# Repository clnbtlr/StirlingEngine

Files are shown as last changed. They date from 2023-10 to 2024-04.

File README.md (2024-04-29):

# StirlingEngine

Repository for the thermodynamic analysis of desktop Stirling engine. An Arduino micro is used to measure the engines internal pressure and flywheel angle. This data is then imported into matlab to determine the heat, work and thermal efficiency. This project is intended as a low-cost demonstration of the different thermodynamic processes in an actual heat engine for physics or engineering students.

Front view:


 
Top view:



## Bill of Materials

| Part                                            | Supplier     | Cost, each (€)|
| ----------------------------------------------- | ------------ |---------------|
| Stirling Engine                                 | Amazon       | 40            |
| Arduino micro                                   | RS           | 26            |
| Mikro-2755 Angle 3 Breakout board               | RS           | 14            |
| MPXV7002DPT1 Pressure Sensor                    | Farnell      | 18            |
| Perma-Proto small mint tin size breadboard      | Adafruit     | 8             |
| Pnuematic tube adapter M5 Male to Push In 4 mm  | RS           | 3             |
| Diametrically magnetised ring magnet Ø 10/5 mm  | supermagnete | 1             |

An Arduino micro was used as it operates at 5V which is the voltage required for the pressure and angle sensors but this could also be substituted for an Arduino Uno.

As well as the above, jumper wires of various lengths, male hearder pins, 4 x M3 screws, and a small length (~ 7 cm) of Ø 4 mm pneumatic tubing are also required.

In addition, some small 3d-printed PLA parts were used. The .stl files are included in the .\stlFiles directory.

| 3d-printed part name     | Qty required |
| ------------------------ | ------------ |
| MagnetHolder.stl         | 1            |
| PermaProtoSmallClip.stl  | 2            |

## Assembly

The pressure sensor was soldered to the perma-proto board such that pin 2 (Vs) and pin 3 (GND) are along the positive and negative power rails. 7 male header pins were soldered in row 3, columns 0-6. Jumper wires were then soldered in place to connect the pressure sensor pins and angle 3 breakout board to the header pins, as shown in the front view photo.

The pinout for the connections is as follows: 

| Arduino micro            | Angle 3 click/AK7451 | MPXV7002DPT1 | Perma-Proto pin |
| ------------------------ | -------------------- | ------------ | --------------- |
| 5V   | 5V  | Vs   | 2 |
| GND  | GND | GND  | 1 |
| SCK  | SCK | -    | 5 |
| MI   | SDO | -    | 4 |
| MO   | SDI | -    | 3 |
| SS   | CS  | -    | 6 |
| A5   | -   | Vout | 0 |

A M5 hole was drilled and taped into the top plate of the engine and the pneumatic adapter with gasket was screwed in place.

The MagnetHolder 3d-printed part acts as a bushing between the ring magnet and the shaft of the flywheel. The magnet was glued onto the 3d-printed part before being pushed onto the shaft up to the cam. See top view photo. No glue was used as the PLA part is intended to be a tight fit.

The 2 x PermaProtoSmallClip 3d-printed parts are used with the 4 x M3 screws to secure the soldered breadboard to the metal vertical bracket. The PLA parts are designed to be self-taped by the M3 screws. Ensure that the AK7451 chip on the Angle 3 click board is lined up with the flywheel axis of rotation, and then tighten the M3 screws sufficiently so everything doesn't move.

Connect the Ø 4 mm pneumatic tubing to the MPXV7002DPT1 pressure sensor port closest to its top surface (port P1 in its datasheet) and the pneumatic adapter in the top plate.

## Arduino Code

The zero position of the angle sensor needs to be set correctly so that during operation, the measured angle increases. The zero position is the angle reading corresponding to the highest point of piston in degrees. It will vary based on how the magnet was assembled to the flywheel shaft. Using the Arduino IDE, uncomment the Serial.print(angle) line in the stirlingEngine.ino sketch and upload it to the Arduino micro.

Slowly rotate the flywheel by hand until the piston is at its maximum height, read the angle value in the Serial monitor and then update the zeroPos variable in the sketch. The Serial.print(angle) line can be commented out now again. Update the geometric variables in the script if necessary for a different model of Stirling engine. Upload the updated sketch to the Arduino micro again.

The real-time values for the pressure and volume can now be monitored in the Serial Plotter window.

## Running a test

Fill a mug with hot water from a kettle. Measure its temperature (i.e. the hot reservoir temperature) using a thermometer/thermistor/thermocouple. Measure ambient temperature (i.e. the cold reservoir temperature). Place the Stirling engine on top of the mug and wait a few minutes for the hot plate to heat up. Then by hand, spin the flywheel and it should start running freely. Direction of rotation is clockwise in the photos above.

The almost sinusodial change in pressure and volume over time should be observed in the Ardunio IDE serial plotter window. The pressure signal leads the volume signal.

## Data analysis with Matlab

In the Matlab script readStirlingData.m (tested on r2019b and r2023a), the measurements from the Arduino can be streamed using serial port communication using the Instrument Control Toolbox (in the absence of this toolbox, the data from the Arduino serial port could also be recorded to a .txt file using PuTTY and then imported into Matlab). The gauge pressure and volume change data for ~12 seconds or ~30 cycles are saved in a .mat file for loading. Two .mat files of data from the Arduino are provided in this repository:

| .mat file name           | Description                               |
| ------------------------ | ----------------------------------------- |
| arduinoData.mat          | P and V data from MPXV7002 sensor         |
| arduinoData1.mat         | P and V data from PSE533 sensor           |

The PSE533 pressure sensor was used to compare/check the values from the MPXV7002 sensor. The values of pressure were sligtly different between the two sensors, most likely as a result of sensor accuracy and precision. Either set of data can be used in the analysis.

The matlab script first plots the time series data from the arduino similar to the Arduino IDE serial plotter, as shown below.

arduinoTimeSeries

It then presents this data as a P-V diagram, with the values for pressure converted from gauge to absolute pressure, and the volume converted from dV to specific volume.

arduinoPV

The ideal Stirling cycle P-V diagram is calculated using the different thermodynamic process relationships and from the measured hot and cold reservoir temperatures and the min. and max. specific volumes. Both the ideal and measured P-v data is plotted and the results show that the actual engine is doing much less net work than the actual cycle due to inefficiencies/irreversibilities.

idealPV

The ideal Stirling cycle T-s diagram is calculated, again using the different thermodynamic process relationships, and the measured P-V data is recalculated into T and s. The values for heat, work and thermal efficiencies are calculated and output to the console. The ideal Carnot efficiency was found to be ~19% while the actual efficiency was ~0.4%.

## Data analysis with Python
The python script readStirlingData.py works in the same fashion as the matlab script. The pressure and volume data from the Arduino is imported from the data.csv file included in the directory. The P-V and T-s values are calculated and followed by plotting of the diagrams. Efficiency results are identical to the matlab results.

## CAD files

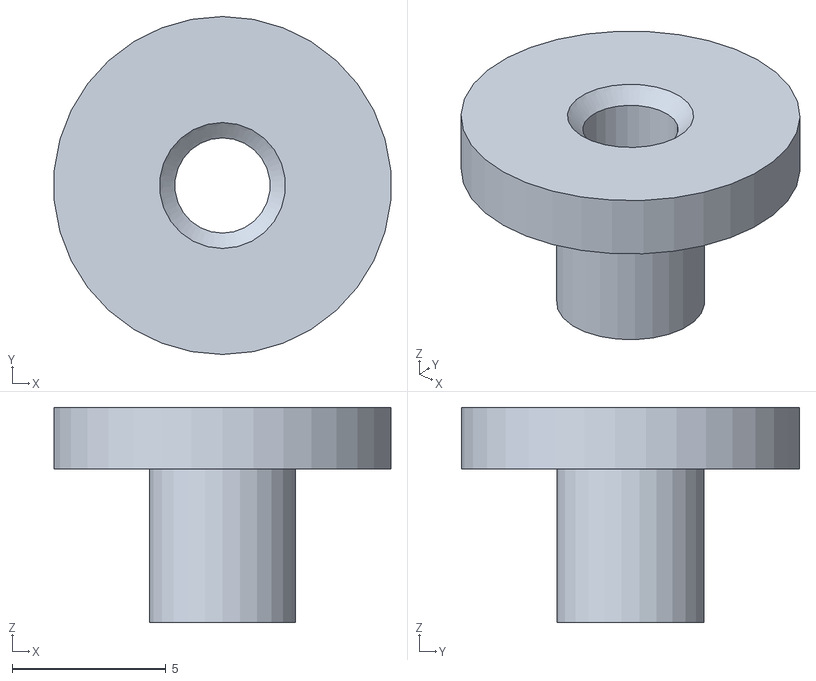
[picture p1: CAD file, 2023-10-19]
stlFiles/MagnetHolder.stl
11.0 x 11.0 x 7.00

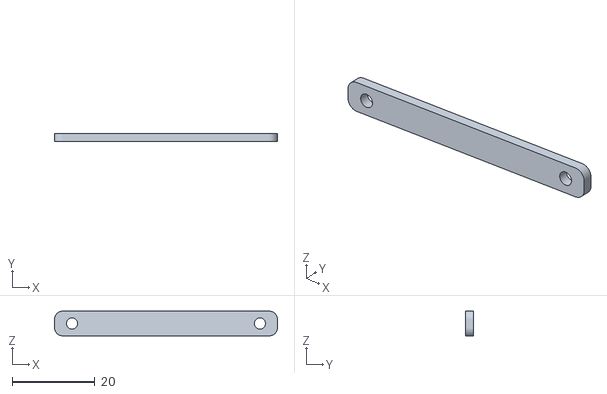
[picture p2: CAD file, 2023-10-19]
stlFiles/PermaProtoSmallClip.STL
54.0 x 2.00 x 6.00

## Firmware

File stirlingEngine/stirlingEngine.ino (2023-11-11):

/* Stirling Engine Pressure and Volume measurement. 
clnbtlr
Oct 2023

Using Arduino Micro as MCB as sensors require 5V.
Pinout:
  AK7451:
  5V <-> 5V
  GND <-> GND
  SCK <-> SCK
  MI <-> SDO
  MO <-> SDI
  SS <-> CS

  MPXV7002DPT1:
  5V <-> VS
  GND <-> GND
  A5 <-> VOUT
*/

#include <SPI.h>
#include "ak7451.h"
AK7451  ak7451;

int r = 4; // offset distance between axis and crank [mm]
int L = 40; // crank arm length [mm]
float A = PI/4.0*sq(16.0); // piston cross sectional area [mm2]
float zeroPos = 123.0; // angle reading corresponding to highest point of piston [deg]
int pressurePin = A5; // analog input pin for pressure sensor

void setup() {
  Serial.begin(19200);
  while(!Serial){ // wait for serial port
    delay(1);
  }
  Serial.println("***Reset***");
  ak7451.begin(SS); // SS pin on Arduino Micro but can be any other Digital I/O Pin
}

void loop() {
  float supply = readVcc()/1000.0; // read Vcc supply
  float angle = ak7451.readAngle(); // read angle from AK7451 sensor
  angle = fmodf(angle+zeroPos,360.0); // removes zeroPos from measured angle and wraps to 360 deg using modulo function
  float pressure = analogRead(pressurePin)*supply/1024.0; // read bits from pressure sensor and convert to voltage
  pressure = (pressure/supply-0.5)/0.2; // convert V to kPa (see MPXV7002 datasheet p.6 for transfer function)
  //pressure = ((pressure)*50.5)-151.5; // convert V to kPa (see PSE533 datasheet 3 for transfer function)
  float h = r*(cos(deg2rad(angle))-L/r*(sqrt(1-(r/L*sq(sin(deg2rad(angle)))))-1)); // change in piston height (see Lu paper, eq.2)
  float volume = A*h/1000.0; // volume change [cm3]
  //Serial.print("angle:"); Serial.print(angle); Serial.print(",");// print angle to Serial Monitor
  //Serial.print("height:");Serial.print(h,3); Serial.print(",");// print height to Serial Monitor
  Serial.print(pressure,3); Serial.print(",");
  Serial.println(volume,3); // print volume to Serial Monitor
  delay(10); // delay between measurements (Lu paper used 200 samples/sec)
}

long readVcc() { // Read supply voltage to improve ADC precision from https://github.com/SensorsIot/ADC_Test.git
  long result;
  // Read 1.1V reference against AVcc
  #if defined(__AVR_ATmega32U4__) || defined(__AVR_ATmega1280__) || defined(__AVR_ATmega2560__)
  ADMUX = _BV(REFS0) | _BV(MUX4) | _BV(MUX3) | _BV(MUX2) | _BV(MUX1);
  #elif defined (__AVR_ATtiny24__) || defined(__AVR_ATtiny44__) || defined(__AVR_ATtiny84__)
  ADMUX = _BV(MUX5) | _BV(MUX0);
  #elif defined (__AVR_ATtiny25__) || defined(__AVR_ATtiny45__) || defined(__AVR_ATtiny85__)
  ADMUX = _BV(MUX3) | _BV(MUX2);
  #else
  ADMUX = _BV(REFS0) | _BV(MUX3) | _BV(MUX2) | _BV(MUX1);
  #endif
  delay(2); // Wait for Vref to settle
  ADCSRA |= _BV(ADSC); // Convert
  while (bit_is_set(ADCSRA, ADSC));
  result = ADCL;
  result |= ADCH << 8;
  result = 1126400L / result; // Calculate Vcc (in mV); 1126400 = 1.1*1024*1000
  return result;
}

float deg2rad(float angle){ // convert degrees to radians
  float rad = angle*PI/180.0;
  return(rad);
}

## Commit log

2023-10-01 first code attempt with spi and angle 3 click board
2023-10-03 updated CS pin
2023-10-03 Added AK7451 pinout for Arduino Micro
2023-10-07 Fixed typo in pin assignments
2023-10-15 Added AK7451 library code and pressure sensor reading
2023-10-15 Improve ADC precision with internal Vref
    https://github.com/SensorsIot/ADC_Test.git
2023-10-15 Update serial print labels
2023-10-19 Uploaded .stl files
    [MagnetHolder-BodyChamfer001.stl, Perma-Proto_Small_clip.STL]
2023-10-19 Moved and renames .stl files
    [MagnetHolder.stl, PermaProtoSmallClip.STL]
2023-10-19 Changed to MPXV7002 sensor
2023-10-22 Update matlab file to calculate ideal cycle
    Matlab file calculates ideal Stirling cycle, and imports arduino data from .mat file to compare the two.
    Arduino data is much lower than the ideal case, but is this normal or an error somewhere...?
2023-10-23 Update files with PSE533 measurements
    Read values from PSE533 compound pressure sensor which measured higher values. Cleaned up Arduino script and changed Matlab plots to kPa.
2023-11-09 Calculated entropy, work and heat
2024-04-28 Added python files
    Added python files and organized into folders.
    [data.csv]
2024-04-28 Updated matlab script
    Tidied entropy definition and plots.
    [data.csv]
2024-05-23 Update stirlingEngine.ino
    Added info about angle zero position calibration from readme.
